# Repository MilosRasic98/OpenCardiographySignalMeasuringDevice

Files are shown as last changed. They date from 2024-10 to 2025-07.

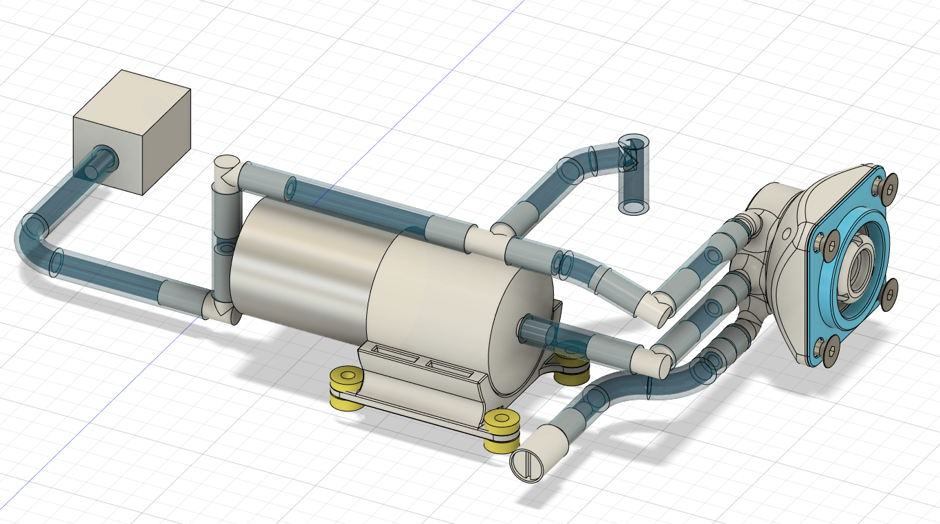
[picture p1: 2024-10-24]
Pictures/Mechanical/cad_pneumatics.PNG

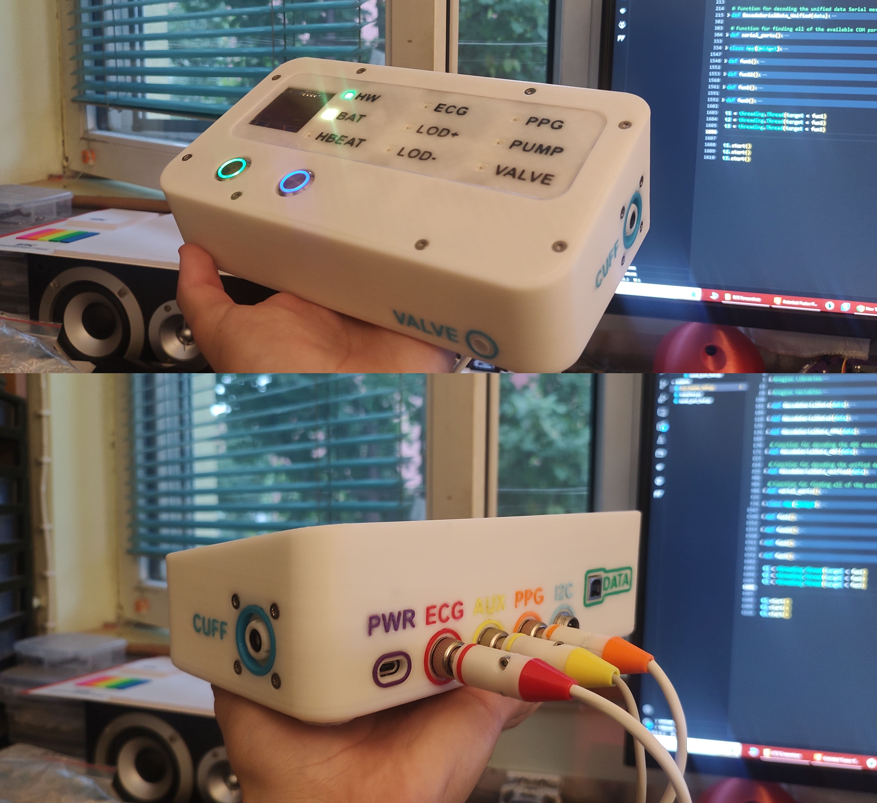
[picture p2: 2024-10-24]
Pictures/Mechanical/finishedproject.jpg

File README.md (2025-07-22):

# OpenCardiographySignalMeasuringDevice

**VIDEO OUT WITH DETAILED PROJECT EXPLANATIONS - CHECK BELOW!**

**DISCLAIMER: THIS IS A DEVICE INTENDED SOLELY FOR RESEARCH PURPOSES AND NOT A MEDICAL DEVICE INTENDED FOR CLINICAL OR DIAGNOSIS USE.**

This repository covers the development process of hardware and software and results analysis, for an open-source Cardiography Signal Measuring Device. On this page, you will be able to find all of the CAD files for the 3D printed parts, Gerber files for PCB fabrication, all of the code needed for the project, and test results of the data analysis. If you have any questions or comments, feel free to contact me! The main goal of the project was to be able to record, store, and analyze these signals:

1. Arm Cuff Air Pressure Signals
2. Electrocardiography Signals (ECG)
3. Phonocardiography Signals (Stethoscope)
4. Photoplethysmography Signals (PPG)

Through this project, I wanted to test out different algorithms for measuring blood pressure either by using just the air pressure signals from the arm cuff or those signals in combination with the other measurements, at the bottom of this page, you can take a look at the results. This project was developed as my Master's Thesis project at the University of Belgrade—School of Electrical Engineering (www.etf.bg.ac.rs), under the mentorship of Prof. Nadica Miljković. In the two pictures below you can see how the finished device looks and the design of the graphical interface for controlling the device.

For more detailed explanations about everything from electronics, to 3D printing, to measurements and data analysis, click the thumbnail below to check out the video!

Watch the video (https://www.youtube.com/watch?v=5UgFEHPnKJY)

Details and discussion about the project can be found on the Element14 Community: [E14 - CardiographyProject](https://community.element14.com/challenges-projects/element14-presents/project-videos/w/documents/71947/building-an-open-source-blood-pressure-heart-signal-monitor----episode-674?ICID=HP-674-Building-an-Open-Source-Blood-Pressure-Signal-Monitor-JULY25-WF4122160)

For things like the BOM and the implemented commands, please check this Google Sheet which is updated as soon as something new is added: https://docs.google.com/spreadsheets/d/1H5B5Kw3XJPlpduM7bu2WPejcbya2c3x0Nj9kcexb-uc/edit?usp=sharing

The project is featured in the MagPi Magazine issue 150, you can check it out here: https://magpi.raspberrypi.com/issues/150

You can take a look at the CAD models and download them from Printables as well:
1. Main Device: https://www.printables.com/model/1052466-open-cardiography-signal-measuring-device 
2. PPG Clamp: https://www.printables.com/model/1052459-ppg-clamp 

finishedproject

ThePerfectScreenshot

## Mechanical Design

The case and all of the necessary components have been 3D printed out of PLA on the Creality K1C, you can find all of the STL files as well as STEP files in the CAD files directory. Since everything was printed on a single-color 3D printer, all of the different colored inlays were glued in during the assembly process. At the back of the device GX12 connectors are used, while there are two additional USB ports, type C for charging, and type B for data (charging currently not validated, more on that later). The case houses the main custom PCB, the 18650 LION battery, and the whole pneumatic setup needed for blood pressure measurement. In the pictures below, you can see the pneumatic setup, as well as how everything is packed inside the case.

cad_pneumatics

cad_inside1

## Electronics

For electronics, a custom 4-layer PCB has been developed that uses the Raspberry Pi Pico W as the microcontroller for controlling everything. In the electronics directory, you can find the full schematics and also find the Gerber files necessary for manufacturing this PCB. The device is controlled over serial communication, and that is also how the data is sent over to the PC. These are some of the main features of the electronics:

1. Isolated USB communication - The USB data connector is galvanically isolated from the rest of the electronics so that it's safe to use, it will act as a normal USB device when connected to a PC.
2. 3V3 Buck-Boost regulator - Ensures that the device stays operational when the battery voltage drops below 3.3 V.
3. 6V boost regulator - Powering the air pump and air valve for the blood pressure measurement process.
4. Pressure Sensor Amplification - For amplifying the signal from the pressure sensor, an instrumentation INA826 amplifier has been used.
5. Stethoscope Conditioning Signals - The original idea was to use a stethoscope with an AUX output, 3 different circuits are present on the PCB for conditioning the signal so that it can be safely measured with the Pi Pico W ADC. There is a DIP switch for disabling individual circuits.
6. AD8232 ECG - The AD8232 is used for measuring the ECG signals, it was designed according to the datasheet for measuring ECG with 3 electrodes so that the signal can be analyzed for morphology.

The PCB can be powered ON by either using a switch or a button and then latching the EN pin on the buck-boost converter using the Raspberry Pi Pico W. The finished PCB design (V1) is shown in the picture below and below that is the PCB during the testing process.

pcb2d

PXL_20240524_074411466~2

For the sake of proper USB isolation and noise reduction around the switching converters, PCB cutouts, and plane breaks were added where necessary, as can be seen in the pictures below.

usbiso

buckboost_layout

### ERRORS

If you plan on pursuing this project further, below are the mistakes found during the testing process.
1. The Q6 transistor in schematic 1-Power has been flipped, meaning that the protection circuit is not validated. A quick fix is to solder a wire from BAT- to GND.
2. The isolated power supply was not working as it was supposed to. - Needs further testing.
3. The pinout on the pressure sensor is wrong.

## Software

The software for this project is currently split into three different codes and is written in C++ and Python. You can find all of the codes in the directory Software on this GitHub repo.

1. Raspberry Pi Pico Firmware - C++ - Arduino IDE -  Code that communicates with the PC over serial, controls all actuators and gathers data from the sensors.
2. Graphical Interface - Python - Visual Studio Code - Code that enables easy use of the device and shows all of the measurements in real-time. It also enables users to record all of the data into a CSV file.
3. Data Analysis - Python - Google Colaboratory - Code that analyses all of the data recorded and stored in the CSV directories.

## Additional Hardware

Besides the main device that has been shown above, there are three more things developed that are used with this device. These include the PPG clamp, a custom stethoscope, and an apparatus for calibrating the pressure sensor. If you intend only to measure ECG signals, none of these are needed, however, if you want to measure the air pressure inside the arm cuff, you'll need a way to calibrate the system, for which the apparatus is used. Also, if you want to have PPG or stethoscope measurements, you'll need them as well.

### PPG Clamp

The mechanical parts of the PPG clamp are 3D printed out of PLA as well, and the clamp is made around a MikroElektronika Oxy 5 Click, which interfaces with the system over I2C. While the outside clamp is not necessary, it provides constant pressure of the finger on the sensor, and it also blocks out outside light which helps with having better measurements. The clamp is shown in the picture below.

ppg_joines

### Stethoscope

The stethoscope that everyone has seen is an analog device that amplifies the sound so that the doctor can listen to different things such as breathing or listen to how the heart is beating. To connect this analog device to the rest of the system, the earphones were removed and a small piezo microphone was inserted into a tube so that it forms an air-tight seal. This microphone was then connected to an amplifier circuit that then goes to the analog pin of our device. The stethoscope is shown in the picture below.

stethoscope_merged

### Pressure Sensor Calibration Apparatus

When looking at the pressure sensor datasheet, the main thing we can see is that it has a linear response to the pressure. The problem here is that we are using a potentiometer to adjust the amplification, so we don't know what voltage translates to what pressure (We can always do calculations based on the potentiometer resistance and the INA826 datasheet, but it's more accurate to confirm using a calibration apparatus). This is why the calibration apparatus has been made, it can be seen in the pictures below.

PXL_20240521_131159092 MV~2

PXL_20240521_131219779 MV~2

The way the apparatus works is by being able to keep a constant pressure in the system that can be adjusted using the two screws pushing the two plungers of the syringes. In the front, there are three air pressure gauges (one is enough, three were used to do cross-validation). We want to use this apparatus by first connecting the apparatus to the pressure sensor on our PCB and then slowly adjusting the potentiometer and the apparatus so that we get to the point where we are reading 3.3 V at 40 kPa (300 mmHg). This ensures that we can cover the whole possible range while measuring blood pressure while also maximizing the capabilities of the ADC on the Pico W. While it would be enough to test in two points since the manufacturer specified a linear response, calibration was done in 40 points to ensure the sensor is working properly. Results of the calibration process are shown below, where the dots show the individual measurements, and the line is estimated using the least mean square method.

GrafikKalibracije

## Testing Process

The testing was done by comparing the results to a commercially available device. For this, the Wellue BP2 was used since it gives the Mean Arterial Pressure (MAP) measurement, besides the Systolic (SYS), Diastolic (DIA), and heart rate (HR) measurements. The person is supposed to first sit on a chair for at least 5 minutes with legs on the floor. After that, the initial measurement with the commercial device should be conducted. When that is complete, there should be at least a minute between consecutive measurements. To properly measure the signals, follow the picture below.

ElectrodePlacement

When everything is connected as shown in the picture below, connect the system using a USB cable. In the GUI connect to the device by selecting the proper COM port and setting the baud rate to 115200. After that, enable the signals you want to record, and start the stream. When you want to start recording the measurements, enter the CSV file name and click record. This can be seen in a short demo video below, click on the picture to open the video.

IMAGE ALT TEXT HERE (https://www.youtube.com/watch?v=Ox0LqK-V76g)

## Results

In this section, I will showcase the results calculated based on the measurements with the device. Before I start showing graphs, I'll give a short introduction to how blood pressure is measured both manually and automatically. This of course is only considering non-invasive methods, and even in 2024, the gold standard for blood pressure measurement is still the manual approach which includes a regular stethoscope and a hand pump.

### Manual Blood Pressure Measurement

Manual blood pressure measurement takes advantage of what is known as Korotkoff sounds. These are the sounds that can be heard using the stethoscope during the process of measuring blood pressure. This process works by putting an arm cuff above the elbow and starting to inflate it using the hand pump. As the pressure inside the cuff goes up, the cuff squeezes the arm and constricts blood flow through the brachial artery, until the pressure in the cuff goes above the SYS pressure. At that moment, blood circulation is cut off. The doctor measuring blood pressure can recognize this by hearing no sounds on the stethoscope, at that moment, he starts opening a small manual valve to slowly let the air out of the cuff. At the moment that the pressure in the cuff equalizes with the SYS pressure, Korotkoff sounds appear, which present themselves as "banging" noises on the stethoscope. The moment the sounds appear is the moment when we look at the gauge and read the SYS pressure. As the pressure continues to drop in the cuff, the Korotkoff sounds will persist as long as the pressure in the cuff is above the DIA pressure. During this time, the blood flow is turbulent. As the pressure in the cuff falls below the DIA pressure, the blood flow becomes linear and the Korotkoff sounds disappear. This is the moment where we read the DIA pressure on the gauge. This process is illustrated in the picture below, where the blue line represents the air pressure in the cuff, while the red line shows the blood pressure we are measuring.

ManualBPM

### Automatic Blood Pressure Measurement

With the advance of technology, many devices with different algorithms have been developed for measuring blood pressure automatically, and are something that can be found in pretty much every household today. One thing to note here is that these devices work on completely unknown algorithms, and there is no proper way of validating the results they calculate. This is why the manual method is still considered a gold standard in 2024 and also why the criteria for blood pressure monitors is rather low. A blood pressure monitor is considered to be in class A (highest class) if its measurements are in +/- 15 mmHg for the SYS pressure in 85% of the measurements. Considering that if the SYS is 135 mmHg, the device is considered working properly if it's between 120 mmHg and 150 mmHg, this poses a big issue of how trustworthy these devices are.

I'll explain here one of the more well-known algorithms for estimating blood pressure which works by analysing the envelope of the signal. To give you a better idea of what I'm talking about, I'll first show you the pressure measurement in the cuff during a blood pressure measurement test, which is shown in the picture below.

BPM_fig2_PritisakUTokuIspumpavanja

The picture above shows only the part of the signal while the arm cuff is deflating. If you take a closer look at the signal, you can see that pulsations start appearing as the pressure decreased, their amplitudes grow, and at one point the amplitude starts going down. This is what we want to analyze but to do that, we need to pass the signal through a high pass filter and detrend the signal. Once we do that, we can estimate an envelope for that signal and continue with the algorithm. The moment in which the envelope reaches its maximum value is the moment in which the air pressure in the cuff is equal to the MAP. Now, according to the algorithm I am using (Sapinsky) we take the value of the MAP amplitude and find the moments in time where the envelope is equal to 40% of MAP and 80% of MAP. These are the moments at which we measure the SYS and DIA pressures. This is illustrated in the picture below.

AutomaticBPM

### Signal Analysis

In this section, I'll give a short demonstration of signal analysis on the measurements I recorded during testing. This will include analyzing the data from the arm cuff, PPG, stethoscope, and ECG. The code I used for analyzing this data as well as a data set that was analyzed here can be found in this GitHub repository, so you can play around with the data if you want! At the end of the signal analysis, I'll show how the results hold up to the commercial device.

#### Arm Cuff Pressure Signal

I'll begin by analyzing the arm cuff pressure signal since that was the main focus of my work. First, in the picture below is the signal in the arm cuff during the whole blood pressure measuring procedure. You can see the pressure rising steeply while the pump is turned on, as well as the pressure going down as the cuff slowly deflates with a sudden release at the very end when the electromagnetic valve is triggered.

BPM_fig1_PritisakUManzetniUTokuMerenja

As mentioned in the algorithm explanation above, we are interested in the part of the signal where the arm cuff is being slowly deflated, as this part of the signal contains the data we are interested in. For this test, the arm cuff was inflated manually to a high pressure, modern devices do a rough estimate of the SYS pressure while inflating the cuff and they inflate it about 30 mmHg above that value and then they start the deflation process. This is done for patient comfort since high pressures can be painful on the arm. In the picture, you can see the part of the signal where the arm cuff is deflating.

BPM_fig2_PritisakUTokuIspumpavanja

Before estimating the envelope, we need to filter the signal first. The two pictures below show the signal filtering process, if you're interested in the details about the filter, check the code where you can see the filter type, order, and cut-off frequency.

BPM_fig8_Detrending

BPM_fig3_PritisakUTokuIspumpavanja-Filtriran

Now that the signal has been filtered, we can estimate the envelope of the signal. Besides the envelope, we can find the peaks in the signal which correlate to the heart beats, so we can calculate the heart rate from them.

BPM_fig5_PritisakUTokuIspumpavanja-Filtriran-Pikovi-Anvelopa

As you can see from the picture above, the signal is not ideal. We don't have the ideal envelope as expected and as was shown in the drawing above. Nevertheless, this signal can still be used for estimating the SYS and DIA pressures. Before we do that, we need to find the max value of the envelope to find the moments for measuring the SYS and DIA pressures. This is shown in the picture below.

BPM_fig6_PritisakUTokuIspumpavanja-Filtriran-Pikovi-Anvelopa-SYS-DIA-MAP

Using those time moments that we calculated based on the graph in the picture above, we can return to the original pressure signal, and see what was the pressure in the arm cuff in those moments. This is how we calculate the MAP, SYS, and DIA, while we use the peaks for calculating the HR. Below is the picture of that, you can see the final results at the bottom of this section with the comparison.

BPM_fig7_PritisakUTokuIspumpavanja-SYS-DIA-MAP

#### Stethoscope Signal Analysis

I wanted to use the signal from the stethoscope as an experimental way of estimating the SYS pressure based on the description of how we measure blood pressure using Korotkoff sounds. My idea was to try and see when the pulsations become somewhat regular, or better said when they start matching the heart rhythm and taking the beginning of that as the moment for reading the SYS pressure. In the two pictures below, you can see the signal from the stethoscope recorded at the same time as the air pressure signal above as well as the stethoscope signal during the arm cuff deflation phase.

AUX_fig1_CeloMerenjePritiska

AUX_fig2_Ispumpavanje

Here I detected the peaks, and you can see a clear difference from the third peak and how there are no missed pulsations. This is the time moment I wanted to use for the SYS pressure and we can also use those peaks to calculate the HR. 

AUX_fig3_Ispumpavanje-Vrhovi

Using the time moment of the third peak, we return to the pressure signal in the arm cuff to read the pressure at that moment.

AUX_fig5_MerenjeSistolnogPritiska

#### PPG Signal Analysis

PPG works by measuring the reflected light at different wavelengths, and based on that signal, we can calculate both the HR and the blood oxygen saturation. For now, I will only look at the signal for measuring the HR, because we can use it really nicely for estimating the DIA pressure. As I've mentioned above when the pressure in the arm cuff is dropping, the blood flow in the arm goes from turbulent to laminar, and the PPG sensor is designed for measurements when the blood flow is laminar. We can see this in the signal by the first flatlining signal, followed by pulsations as the laminar blood flow returns to the arm. In the two pictures below, you can see the PPG signal from the whole measurement and then only from the section where the arm cuff is deflating.

PPG_fig1_FotopletizmografskiSignalUTokuMerenjaKrvnogPritiska

PPG_fig2_FotopletizmografskiSignalUTokuIspumpavanjaManzetne

I then passed the signal through a filter in the same way I did with the pressure signal shown above. So the two pictures below show the signal filtering process.

PPG_fig6_Detrending

PPG_fig3_FiltriranPPGSignal

What we want to do now is find the peaks in the signal to find the moment when the pulsations appear again. This is the moment we will use to measure the DIA pressure. This is shown in the pictures below.

PPG_fig4_FiltriranPPGSignal-Vrhovi

PPG_fig5_PPG-IzmerenDijastolniPritisak

#### ECG Signal Analysis

In the end, we have the ECG signal. While there is some experimental work for measuring blood pressure by measuring the time delay between R peaks in the ECG signal and the pulsations on the PPG, I will only use the ECG to validate the HR measurement of the other methods and show the morphology of a recorded heartbeat. A section of the measurement is shown in the picture below.

ECG_fig2_EKG_DeoMerenja

By detecting the R peaks, we can easily calculate the HR. We can also use that data from ECG to analyze heart rate variability which is a topic I won't be getting into here. But you can see the time between heartbeats in the picture below.

ECG_fig3_EKG_HRV

And in the end, you can see a single heartbeat that was extracted from the measurement.

ECG_fig4_EKG_JedanOtkucaj

### Final Results

Before showing you the final results from the signal analysis, let's take a look at the measurement done with the Wellue BP2 Blood Pressure monitor. Its results are shown in the picture below.



Now, let's compare that to the results we estimated from our measurements, this is shown in the table below.

| | Mean Arterial Pressure (MAP) [mmHg] | Systolic Pressure (SYS) [mmHg]  | Diastolic Pressure (DIA) [mmHg] | Heart Rate (HR) [BPM] |
| ------------- | ------------- | ------------- | ------------- | ------------- |
| Wellue BP2 | 93 | 130 | 72 | 81 |
| Arm Cuff Air Pressure | 91 | 132 | 79 | 78 |
| Stethoscope | X | 143 | X | 80 |
| PPG | X | X | 75 | 80 |
| ECG | X | X | X | 80 |

As you can see from the table, the results obtained from the data analysis are pretty good when compared to the commercial device. This is of course one data set and all of this requires much more testing, but it's still rewarding to see promising results. Estimating the SYS pressure using the stethoscope didn't give the best estimation, but this needs more experimenting with things like stethoscope placement, pressure, and so on. One thing that gave really good results was the PPG estimation of the DIA pressure, it's more spot-on than the analysis of the pressure in the arm cuff.

If you have any comments or questions about anything you've seen here, feel free to write to me! Some of the pictures have writing in Serbian but the graphs should be clear based on the units, if you're still struggling with any of that, feel free to contact me!

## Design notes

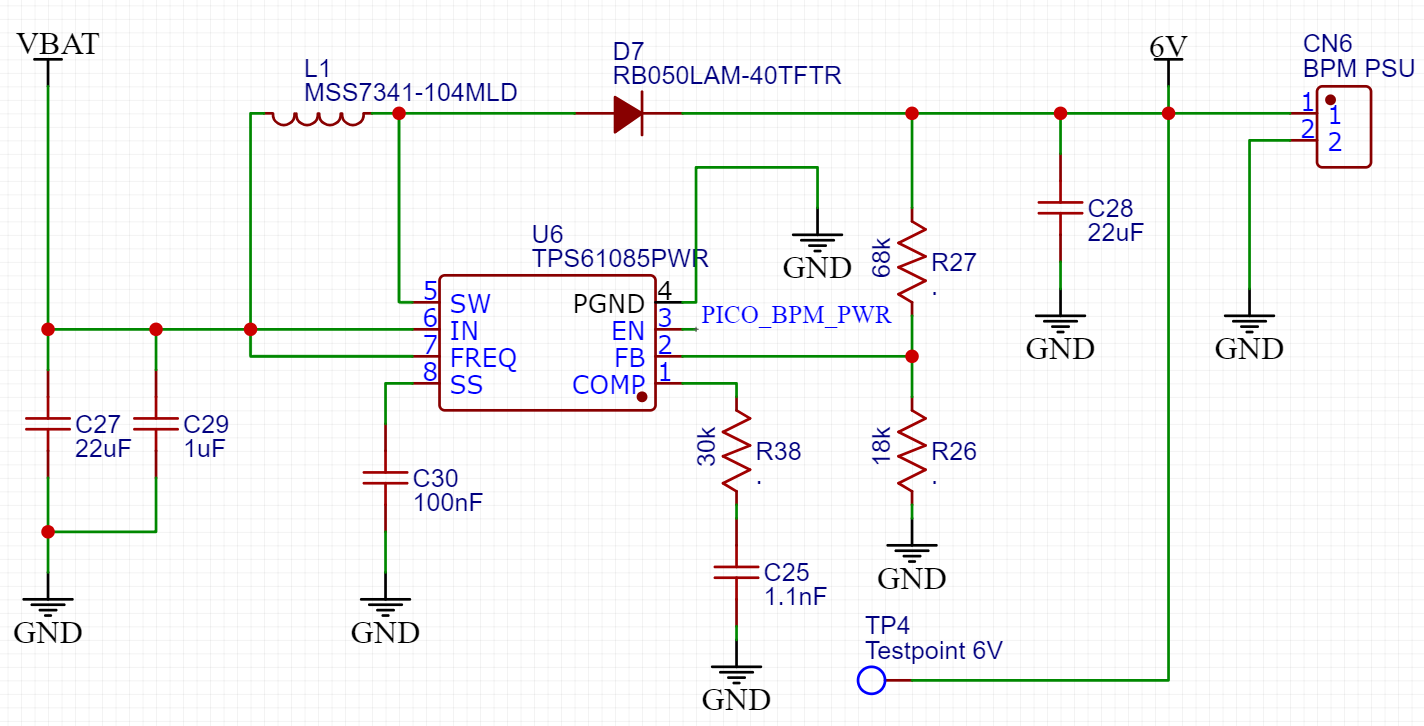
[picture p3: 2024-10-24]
Pictures/Electronics/boost.PNG

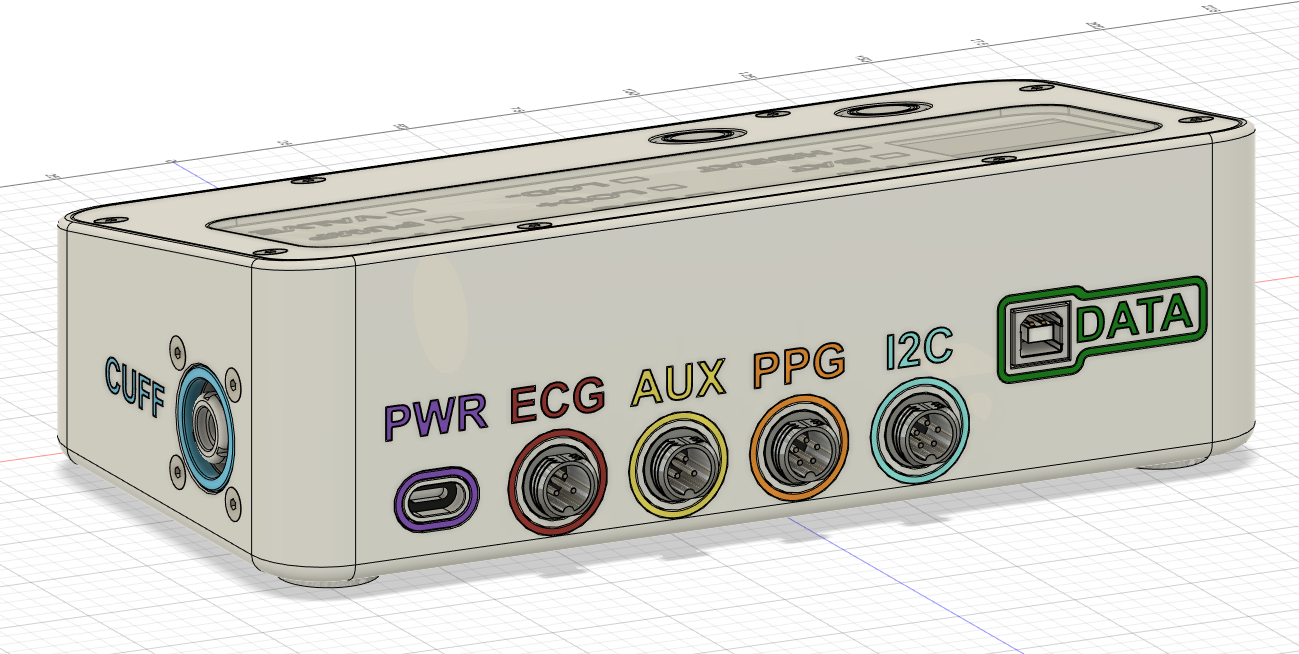
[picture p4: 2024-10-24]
Pictures/Mechanical/cad_backview.PNG

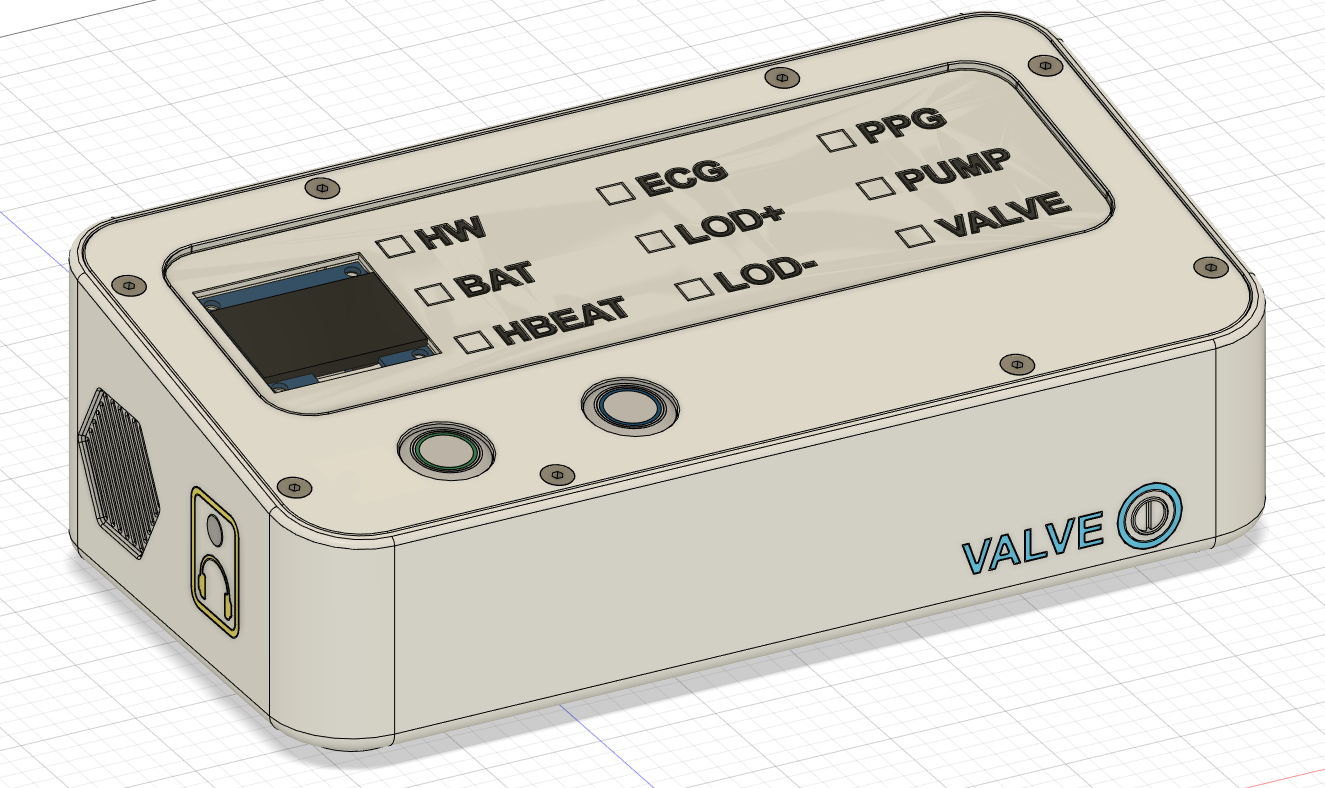
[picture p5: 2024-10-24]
Pictures/Mechanical/cad_frontview.PNG

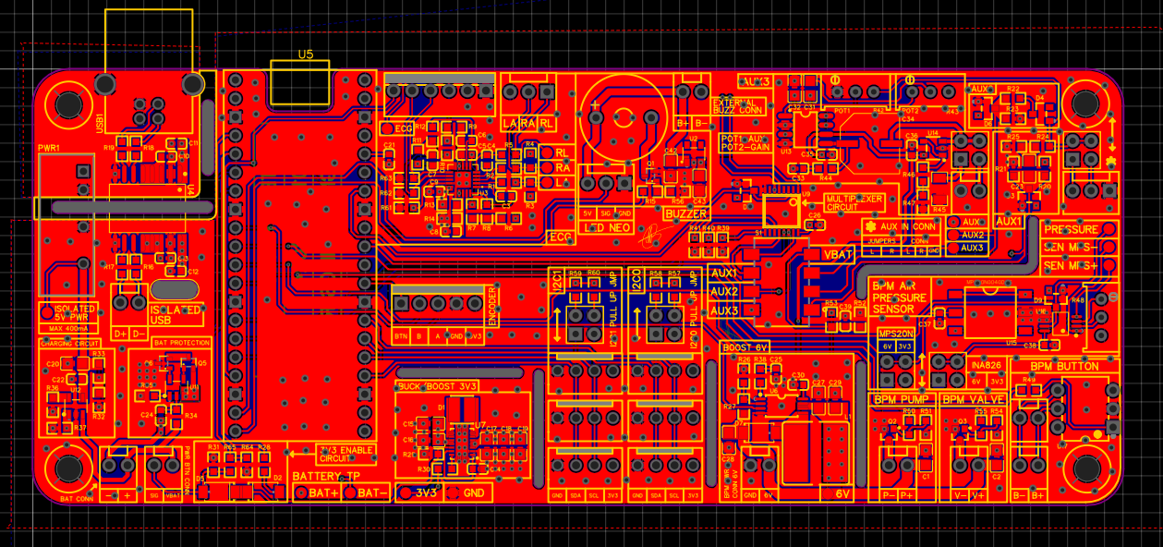
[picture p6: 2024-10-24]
Pictures/Electronics/PCB_1_TopLayer.PNG

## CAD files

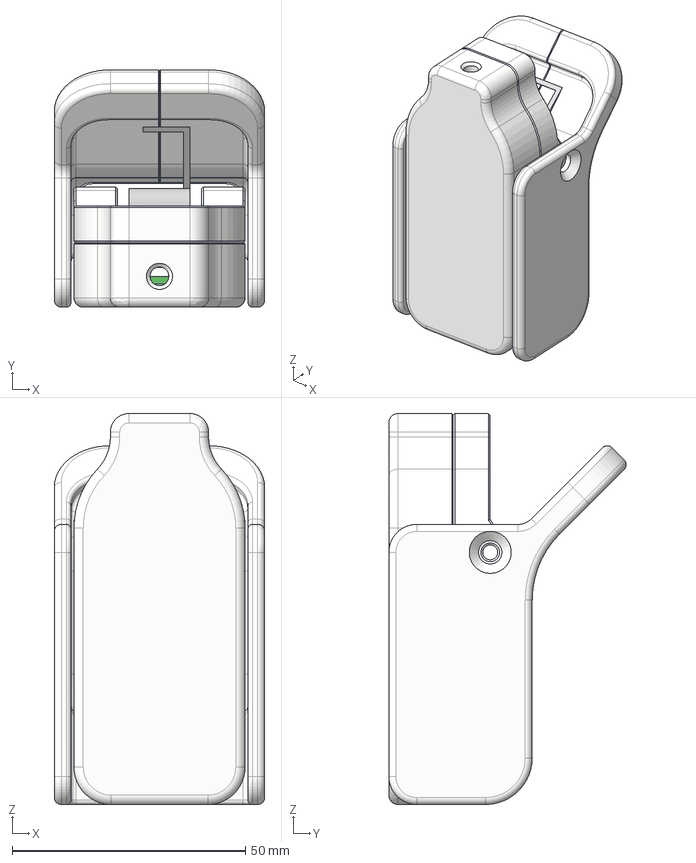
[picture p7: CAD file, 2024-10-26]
CAD/PPG/STEP/Oximeter Clamp V1 v3.step
45.1 x 50.9 x 83.8 mm
Board
User_Library-SMD_CAPACITOR0402 x 7
User_Library-SMD_CAPACITOR0603 x 3
led_0805_green
User_Library-SOT23-6-2
MAX30101
User_Library-PinHeaderX5-1_PinHeaderX5_Body_1 x 4
User_Library-PinHeaderX5-1_PinHeaderX5_Pins_1 x 4
User_Library-R_0805 x 2
User_Library-R_0402 x 6
User_Library-US8_Package_(8US8_8SM8_8DSBGA)_2_4x2_1x0_9
Sot353
Perfboard
Lower Body
Axle Mount
Spring
Cover V1 Half 2
Cover V1 Half 1

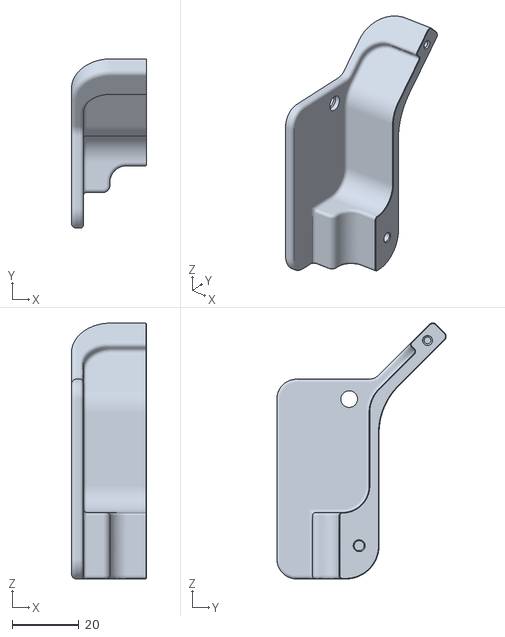
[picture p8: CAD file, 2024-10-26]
CAD/PPG/STL/Cover V1 Half 2.stl
22.5 x 50.9 x 76.9

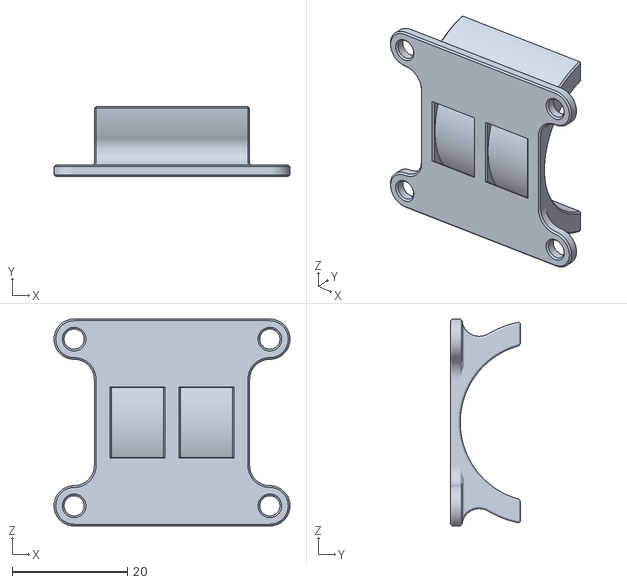
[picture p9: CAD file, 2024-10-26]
CAD/STL/Air Pump Mount.stl
41.0 x 12.2 x 36.0

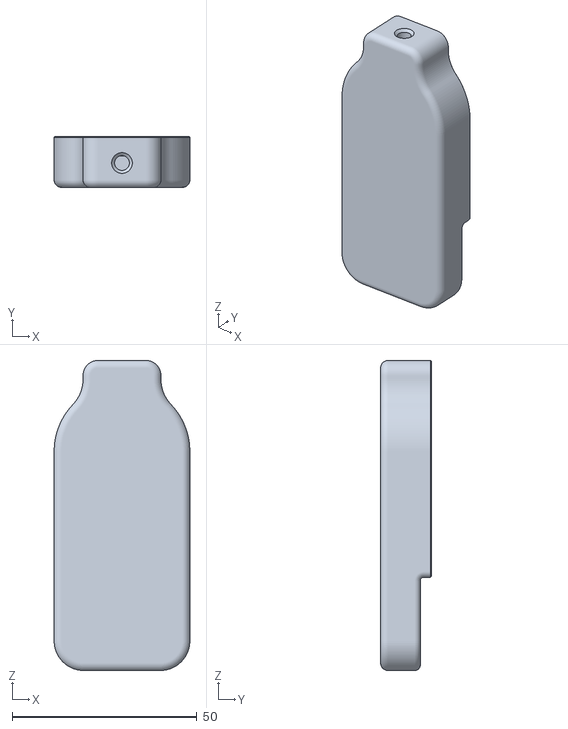
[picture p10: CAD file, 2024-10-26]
CAD/PPG/STL/Lower Body.stl
36.7 x 13.7 x 83.8

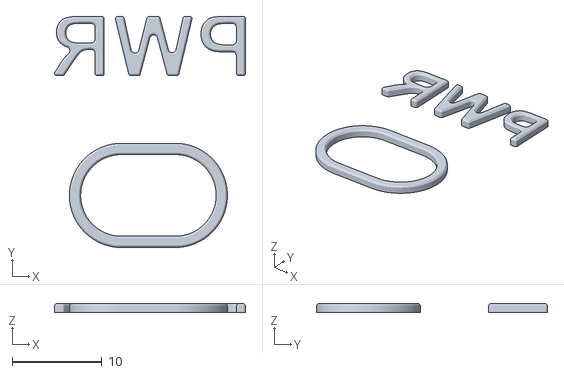
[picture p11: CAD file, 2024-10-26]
CAD/STL/PWR Sign and Ring.stl
21.3 x 25.8 x 1.00

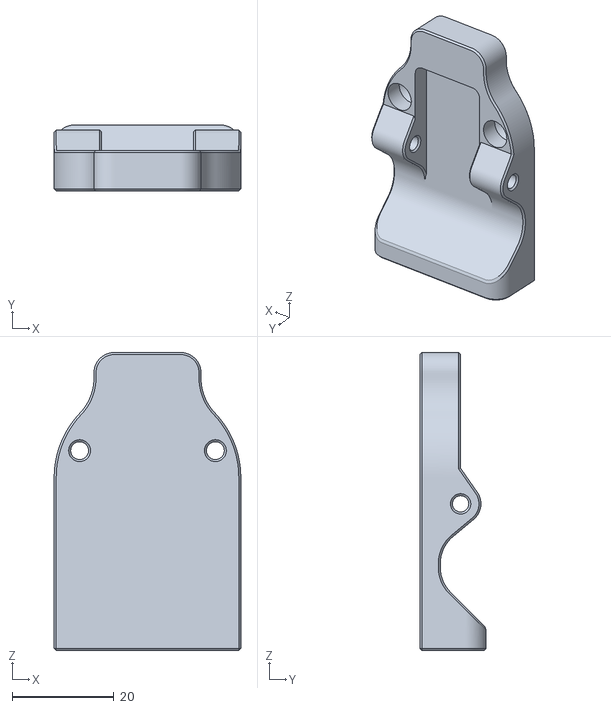
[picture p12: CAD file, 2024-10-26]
CAD/PPG/STL/Axle Mount.stl
36.7 x 13.0 x 58.6

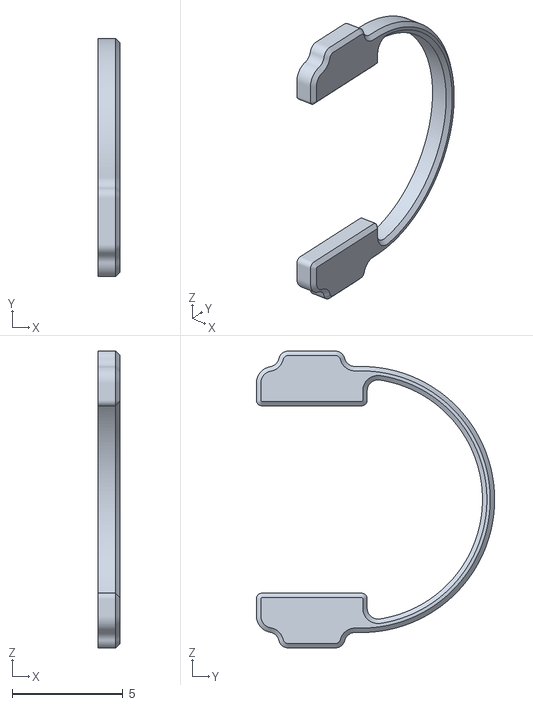
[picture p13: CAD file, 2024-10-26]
CAD/STL/Headphones Sign.stl
1 x 10.7 x 13.4

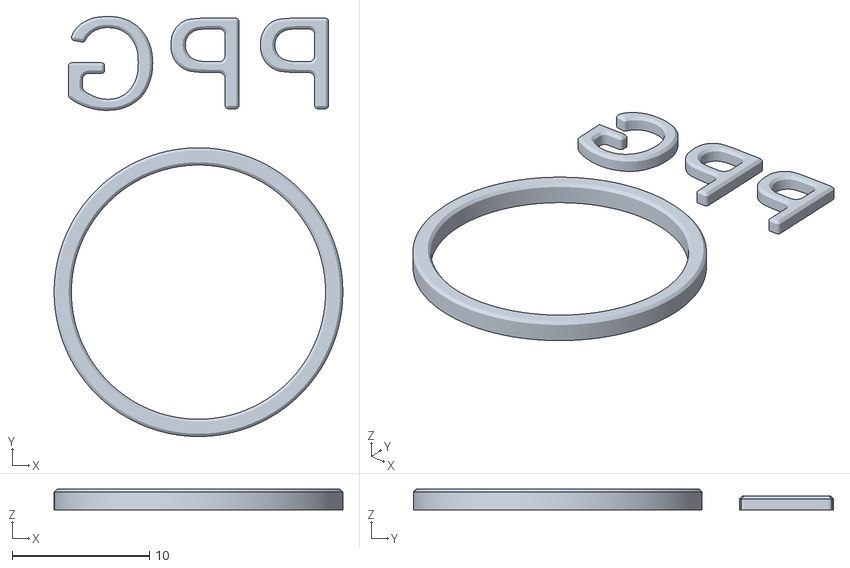
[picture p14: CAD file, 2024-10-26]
CAD/STL/PPG Sign and Ring.stl
21.0 x 30.6 x 1.50

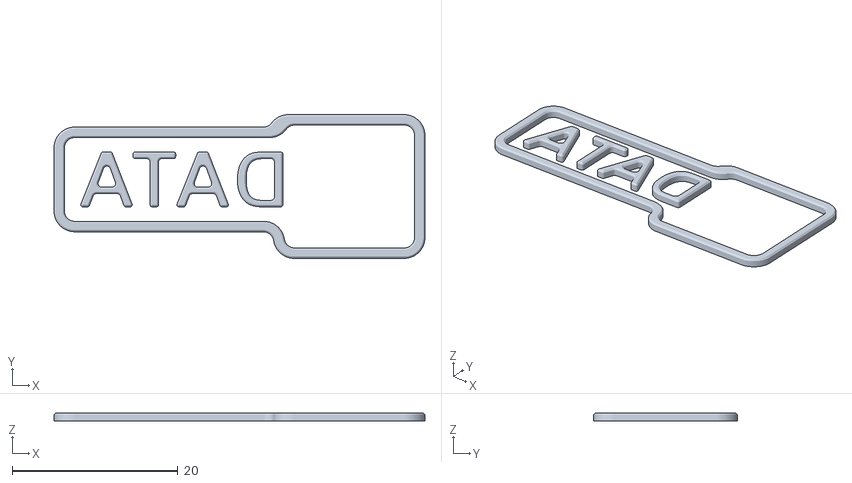
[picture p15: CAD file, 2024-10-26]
CAD/STL/Data Sign and Ring.stl
44.7 x 17.3 x 1.00

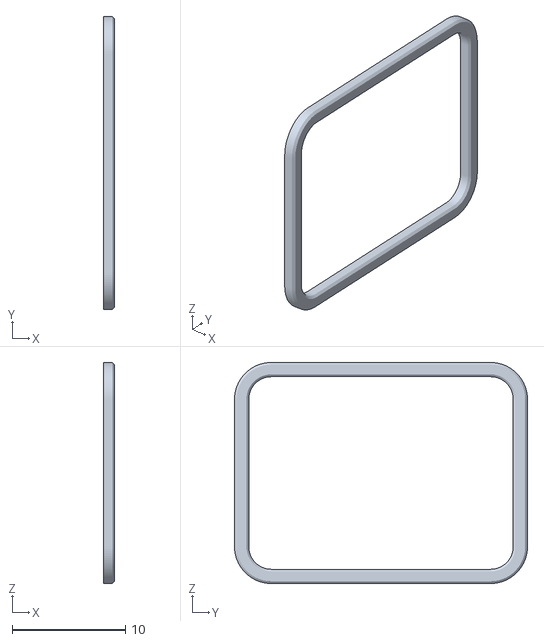
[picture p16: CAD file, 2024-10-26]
CAD/STL/Headphone Ring.stl
1 x 25.9 x 19.5

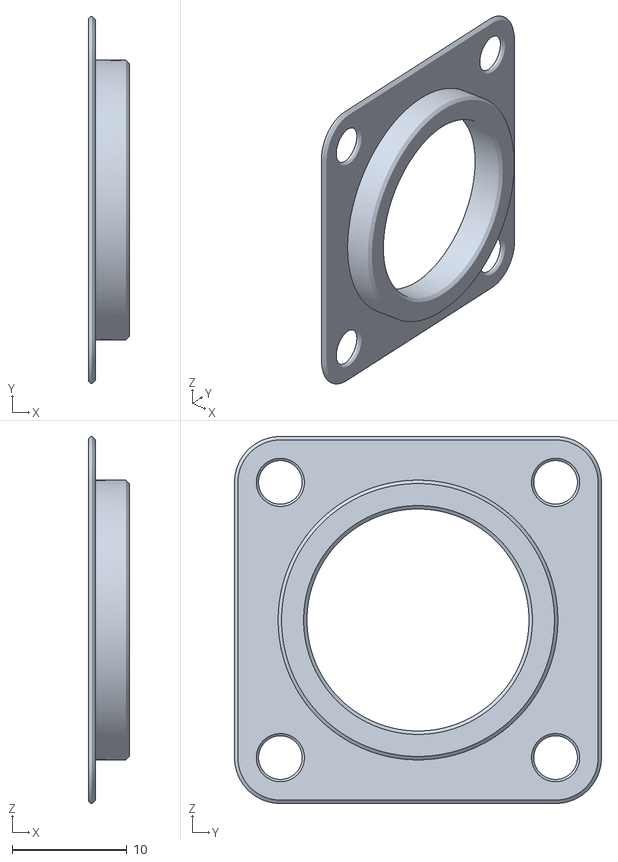
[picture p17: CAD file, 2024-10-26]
CAD/STL/Body End Triple Pipe Blue Top.stl
3.54 x 32.0 x 32.0

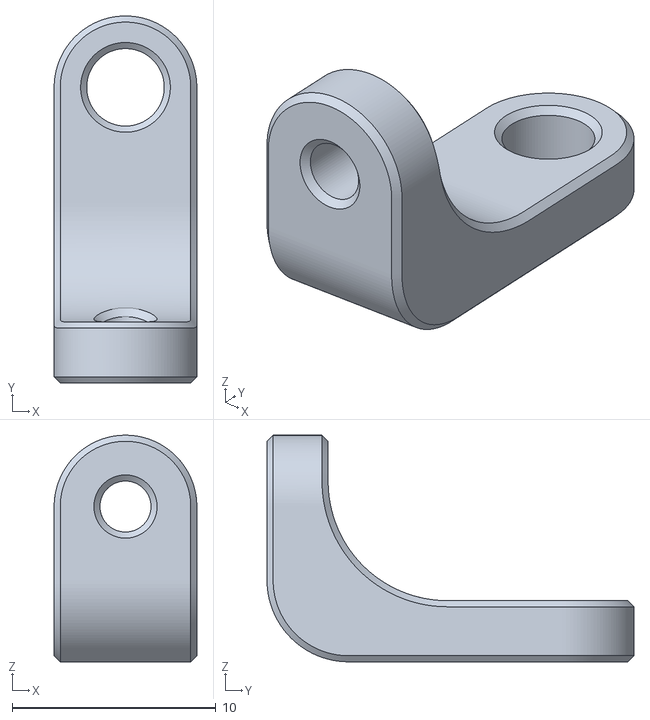
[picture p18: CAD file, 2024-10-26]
CAD/STL/PCB Bracket.stl
7.00 x 18.0 x 11.1

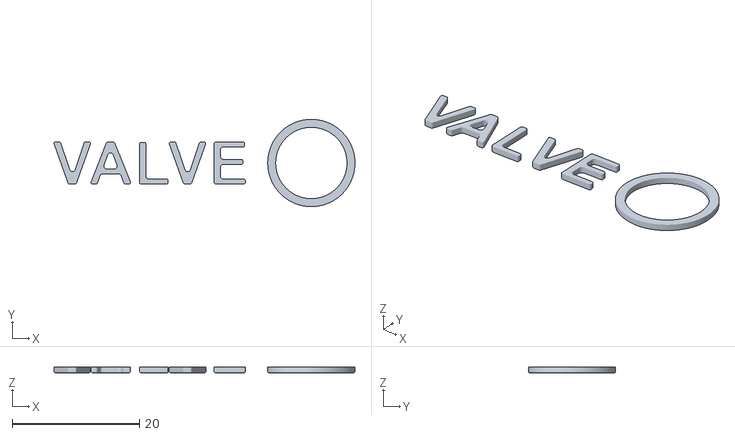
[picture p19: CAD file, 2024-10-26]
CAD/STL/Valve Sign and Ring.stl
47.3 x 13.7 x 1.00

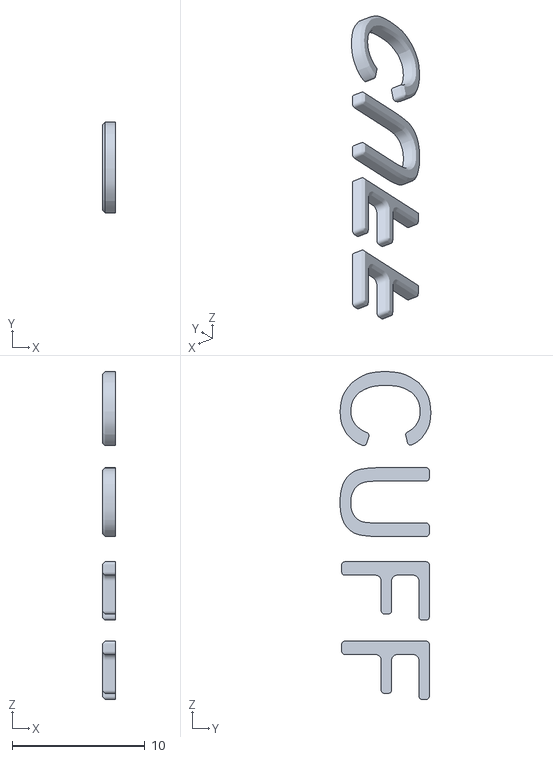
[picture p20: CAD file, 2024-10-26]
CAD/STL/Cuff Sign.stl
1.00 x 6.84 x 24.7

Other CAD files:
CAD/PPG/STL/Cover V1 Half 1.stl
CAD/STL/ECG Sign and Ring.stl
CAD/STL/Body End Triple Pipe Shortened.stl
CAD/STL/LED and Screen Bracket.stl
CAD/STL/AUX Sign and Ring.stl
CAD/STL/Audio Jack Mounting Bracket.stl
CAD/STL/Body Bottom Part V1.stl
CAD/STL/Em Valve Bracket.stl
CAD/STL/I2C Sign and Ring.stl
CAD/STL/Lid.stl

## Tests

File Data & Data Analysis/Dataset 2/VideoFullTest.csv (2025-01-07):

ECG_VALUE | ECG_TIME | BPM_VALUE | BPM_TIME | AUX_VALUE | AUX_TIME | PPG_VALUE | PPG_TIME
1892 | 856347 | -4.865679999999999 | 856347 | 51 | 856347 | 62522 | 856348
1792 | 856349 | -4.94256 | 856349 | 51 | 856349 | 62483 | 856350
1987 | 856365 | -4.94256 | 856365 | 52 | 856365 | 62408 | 856359
1899 | 856371 | -4.865679999999999 | 856371 | 51 | 856371 | 62378 | 856369
1961 | 856381 | -4.94256 | 856381 | 51 | 856381 | 62447 | 856379
2070 | 856401 | -4.865679999999999 | 856401 | 51 | 856401 | 62449 | 856399
2050 | 856405 | -4.865679999999999 | 856405 | 51 | 856405 | 62449 | 856399
1987 | 856407 | -4.865679999999999 | 856407 | 51 | 856407 | 62451 | 856407
1931 | 856409 | -4.94256 | 856409 | 51 | 856409 | 62461 | 856409
1890 | 856411 | -4.94256 | 856411 | 51 | 856411 | 62461 | 856409
1896 | 856415 | -5.0194399999999995 | 856415 | 51 | 856415 | 62461 | 856409
1948 | 856417 | -4.94256 | 856417 | 51 | 856417 | 62470 | 856417
2025 | 856419 | -4.94256 | 856419 | 51 | 856419 | 62485 | 856419
2112 | 856421 | -4.94256 | 856421 | 51 | 856421 | 62485 | 856419
2185 | 856425 | -4.865679999999999 | 856425 | 52 | 856425 | 62485 | 856419
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

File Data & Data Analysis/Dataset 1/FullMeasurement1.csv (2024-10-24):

ECG_VALUE | ECG_TIME | BPM_VALUE | BPM_TIME | AUX_VALUE | AUX_TIME | PPG_VALUE | PPG_TIME
2069 | 204485 | -4.7888 | 204485 | 53 | 204485 | 64514 | 204479
2113 | 204489 | -4.7888 | 204489 | 52 | 204489 | 64533 | 204489
2043 | 204499 | -4.711919999999999 | 204499 | 53 | 204499 | 64582 | 204497
2067 | 204519 | -4.7888 | 204519 | 54 | 204519 | 64602 | 204520
2033 | 204541 | -4.7888 | 204541 | 53 | 204541 | 64590 | 204542
2133 | 204549 | -4.63504 | 204549 | 53 | 204549 | 64596 | 204550
2132 | 204551 | -4.7888 | 204551 | 53 | 204551 | 64620 | 204552
2048 | 204559 | -4.711919999999999 | 204559 | 53 | 204559 | 64606 | 204560
2033 | 204561 | -4.7888 | 204561 | 53 | 204561 | 64629 | 204562
2083 | 204569 | -4.558160000000001 | 204569 | 53 | 204569 | 64616 | 204570
2096 | 204571 | -4.7888 | 204571 | 52 | 204571 | 64600 | 204572
2049 | 204579 | -4.711919999999999 | 204579 | 52 | 204579 | 64619 | 204580
2042 | 204581 | -4.711919999999999 | 204581 | 53 | 204581 | 64607 | 204582
2106 | 204589 | -4.7888 | 204589 | 53 | 204589 | 64621 | 204590
2120 | 204591 | -4.7888 | 204591 | 53 | 204591 | 64569 | 204592
2061 | 204599 | -4.711919999999999 | 204599 | 53 | 204599 | 64632 | 204600
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

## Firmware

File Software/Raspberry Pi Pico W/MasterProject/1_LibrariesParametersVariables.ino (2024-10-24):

/*
 *  LIBRARIES
 */
#include <Wire.h>
#include "RPi_Pico_TimerInterrupt.h"
#include "RP2040_PWM.h"
#include <DFRobot_MAX30102.h>
#include <FastLED.h>

/*
 *  PINS
 */
#define PIN_PWR_BTN     2
#define PIN_PWR_LATCH   3
#define PIN_SIG_CHARGE  4
#define PIN_MCP_CHARGE  5
#define PIN_BPM_PWR     6
#define PIN_BPM_BTN     7
#define PIN_BPM_PUMP    8
#define PIN_BPM_VALVE   9
#define PIN_MUX_A       10
#define PIN_MUX_B       11
#define PIN_MUX_C       12
#define PIN_ECG_EN      13
#define PIN_NEO_LED     14
#define PIN_BUZZ        15
#define PIN_ENC_A       16
#define PIN_ENC_B       17
#define PIN_I2C1_SDA    18
#define PIN_I2C1_SCL    19
#define PIN_I2C0_SDA    20
#define PIN_I2C0_SCL    21
#define PIN_ENC_BTN     22
#define PIN_BPM_ANALOG  26
#define PIN_ECG_ANALOG  27
#define PIN_AUX_ANALOG  28


/*
 *  PARAMETERS
 */

// GENERAL PARAMETERS
#define SAMPLING_FREQUENCY    1000      // [Hz]           Sampling frequency for the Pico ADC
#define COMM_FREQUENCY        500       // [Hz]           Communication frequnecy with the PC
#define ADC_RES               12        // [bit]          ADC resolution set in bits 10/12
#define SERIAL_BAUDRATE       115200    // [#]            Serial communication baudrate 9600/115200
#define PWM_FREQUENCY         1000      // [Hz]           PWM signal frequency     
#define SERIAL_DEBUG          true      // [true/false]   Flag that enables/disables serial debugging
#define LED_FREQUENCY         100       // [Hz]           LED timer 0 frequency
#define CON_FREQUENCY         1000      // [Hz]           Control timer 2 frequency
#define LED_TICKS             100       // [#]            Number of timer ticks before changing the LED state in normal state
#define LED_TICKS_ERROR       10        // [#]            Number of timer ticks before changing the LED state in error state
#define UNIFIED_MESSAGE       true      // [true/false]   Flag for sending a unified message over the serial port
#define PWR_OFF_HOLD          5000      // [ms]           Number of miliseconds that the blue buttons needs to be held for to turn off the device
#define NUM_LEDS              9         // [#]            Number of LEDs on the front panel

// BPM PARAMETERS
#define BPM_MAX_PUMP_DUTY     100       // [%]            Max duty cycle of the PWM signal that is controlling the pump for the BPM
#define BPM_MIN_PUMP_DUTY     0         // [%]            Min duty cycle of the PWM signal that is controlling the pump for the BPM

// AUX PARAMETERS
#define AUX_MAX_BUZZ_DUTY     100       // [%]            Max duty cycle of the PWM signal that is controlling the Buzzer
#define AUX_MIN_BUZZ_DUTY     0         // [%]            Min duty cycle of the PWM signal that is controlling the Buzzer
#define AUX_BUZZ_BEEP_DUTY    10        // [%]            Duty cycle used for the regular beeping when for example when it's indicating the pulse
#define AUX_BUZZ_BEEP_MAX     2000      // [ms]           Length of the longest allowed beep for the buzzer
#define AUX_BUZZ_BEEP_MIN     10        // [ms]           Length of the shortest allowed beep for the buzzer

// PPG PARAMETERS
#define PPG_SPO2_FREQUENCY    1         // [Hz]           Reading frequency for the SpO2 
#define PPG_IR_FREQUENCY      20        // [Hz]           Reading frequency for the PPG sensor

// CALCULATED PARAMETERS
#define COMM_PERIOD           1000000 / COMM_FREQUENCY                  // [us]   Number of us needed to achieve the desired frequency
#define LED_PERIOD            1000000 / LED_FREQUENCY                   // [us]   Number of us needed to achieve the desired frequency
#define SEN_PERIOD            1000000 / SAMPLING_FREQUENCY              // [us]   Number of us needed to achieve the desired frequency
#define CON_PERIOD            1000000 / CON_FREQUENCY                   // [us]   Number of us needed to achieve the desired frequency
#define PPG_SPO2_COUNT        SAMPLING_FREQUENCY / PPG_SPO2_FREQUENCY   // [#]    Max count value for the PPG SPO2 reading
#define PPG_IR_COUNT          SAMPLING_FREQUENCY / PPG_IR_FREQUENCY     // [#]    Max count value for the PPG IR reading

/*
 * VARIABLES
 */

// Flags
bool          flag_en_6V      =       true;     // [true/false]   Flag for turning the boost converter ON/OFF
bool          flag_pin_cng    =       false;    // [true/false]   Flag for indicating if a digital pin state change is needed
bool          error_state     =       false;    // [true/false]   Flag that indicates whether we are in an error state or not
bool          flag_pwr_latch  =       true;     // [true/false]   Flag that indicates whether we should keep the Pico W turned ON or not
bool          led_disable     =       false;    // [true/false]   Flag that indicates whether LEDs are disabled or not

// Communication
bool          flag_new_msg    =       false;    // [true/false]   Flag for showing if there is a new message on the Serial port
String        serial_msg      =       "";       // [String]       Variable for storing the message from the Serial port (Commands are received through this message)       
bool          data_stream     =       false;    // [true/false]   Flag for showing if the data stream to the PC is turned ON or OFF
volatile int  message_id      =       0;        // [#]            In the data stream, this will be the parameters used to make sure there aren't any skipped messages
String        stream_msg      =       "";       // [String]       Variable for storing the message for the DataStream
volatile bool flag_adc_msg    =       false;    // [true/false]   Flag for showing whether a new ADC message is scheduled
volatile bool flag_ppg_msg_ir =       false;    // [true/false]   Flag for showing whether a new PPG IR message is scheduled
volatile bool flag_ppg_msg_o2 =       false;    // [true/false]   Flag for showing whether a new PPG SpO2 message is scheduled       
volatile int  message1_id     =       0;        // [#]            Counter for message with ID = 1
volatile int  message2_id     =       0;        // [#]            Counter for message with ID = 2
volatile int  message3_id     =       0;        // [#]            Counter for message with ID = 3

// Blood Pressure Monitor
int           bpm_pump_duty   =       0;        // [%]            Duty cycle that is being sent to the pin connected to the BPM pump
int           bpm_valve       =       0;        // [0/1]          Variable for storing whether the valve is ON or OFF
int           bpm_opto        =       0;        // [0/1]          Variable for storing whether the optocoupler is turned ON or OFF
volatile int  bpm_adc         =       0;        // [ADC]          BPM ADC reading
volatile int  bpm_mmhg        =       0;        // [mmHg]         BPM reading converted to mmHg
bool          bpm_enable      =       false;    // [true/false]   Flag for inticating whether the BPM readings are enabled or not

// ECG
bool          flag_en_ecg     =       false;    // [true/false]   Flag for turning the ECG chip ON/OFF 
volatile int  ecg_adc         =       0;        // [ADC]          Variable for storing the latest ecg value read by the ADC
int           ecg_lp          =       -1;       // [0/1]          ECG LP signal
int           ecg_ln          =       -1;       // [0/1]          ECG LN signal
volatile int  ecg_msg_time    =       0;        // [ms]           ECG signal read time

// AUX
volatile int  aux_adc         =       0;        // [ADC]          ADC reading for the AUX channel
bool          aux_enable      =       false;    // [true/false]   Flag for indicating whether the AUX readings are enabled or disabled

// SpO2
bool          spo2_active     =       false;    // [true/false]   Flag that indicated whether our sensor is active or not
volatile int  spo2_ir         =       0;        // [#]            Variable for storing the IR value read by the MAX30102 sensor
volatile int  spo2_r          =       0;        // [#]            Variable for storing the R value read by the MAX30102 sensor
int32_t       spo2_o2         =       0;        // [#]            Variable for storing the O2 value read by the MAX30102 sensor
int8_t        spo2_o2_valid   =       0;        // [0/1]          Flag that indicates whether the O2 saturation reading is valid 
int32_t       spo2_hr         =       0;        // [#]            Variable for storing the heart rate value calculated by the MAX30102 sensor
int8_t        spo2_hr_valid   =       0;        // [0/1]          Flag that indicates whether the HR calculation is valid
volatile int  spo2_count      =       0;        // [#]            Counter for lowering the read frequency for SpO2 and HR for the MAX30102 sensor
volatile int  spo2_ir_count   =       0;        // [#]            Counter for lowering the read frequenct for IR readings for the MAX30102 sensor         
volatile int  spo2_ir_time    =       0;        // [ms]           Time of reading the IR signal from the MAX30102
volatile int  spo2_o2_time    =       0;        // [ms]           Time of reading the SpO2 values from the MAX30102
volatile int  ppg_msg_ind     =       0;        // [0/1]          Indicator for a new PPG message
bool          ppg_in_loop     =       true;     // [true/false]   Flag for determening whether PPG is handled in a loop or a timer

// Interface
int           buzz_duty       =       0;        // [%]            Duty cycle for controlling the volume of the buzzer
int           beep_start      =       0;        // [ms]           Start of the beep in ms
int           beep_length     =       0;        // [ms]           Length of the beep in ms
bool          beep_flag       =       false;    // [true/false]   Flag indicating whether we have a new beep or not
int           blue_btn_start  =       0;        // [ms]           Start time for when the blue button has been pressed
bool          blue_btn_state  =       false;    // [true/false]   Flag for indicating whether the blue button is pressed or not

// General
volatile int  led_counter     =       0;        // [#]            Used as a counter to keep track of progress with the LED timer
int           pico_led        =       0;        // [0/1]          Variable which shows whether the Pico LED is ON or OFF
float         battery_voltage =       0.00;     // [V]            Variable used for storing the measured votlage of the LION cell

// Testing
bool          plotter         =       false;    // [true/false]   Flag which indicates if the plotter is active for testing purposes

/*
 *      SPO2 SENSOR
 */
DFRobot_MAX30102            spo2_sensor;        // SpO2 Sensor MAX30102

/*
 *      TIMERS 
 */
RPI_PICO_Timer              TimerLED(0);        // Timer for the heartbeat LED                          - Frequency set in setup() - Default 10 Hz
RPI_PICO_Timer              TimerCOM(1);        // Timer for setting the communication rate             - Frequency set in setup() - Default 0.5 kHz
RPI_PICO_Timer              TimerPPG(2);        // Timer for PPG measurements                           - Frequency set in setup() - Default 2 kHz
RPI_PICO_Timer              TimerSEN(3);        // Timer for sensor data acqusition                     - Frequency set in setup() - Default 2 kHz

/*
 *      PWM
 */
RP2040_PWM*                 PWM_Instance[2];    // PWM for the Pico

/*
 *      LED-s
 */
CRGB                        leds[NUM_LEDS];     // LEDs in the front
 

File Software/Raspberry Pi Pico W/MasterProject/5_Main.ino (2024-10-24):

void setup() {
  // Starting up the Serial Monitor
  Serial.begin(SERIAL_BAUDRATE);
  delay(500);
  Serial.println("Starting the configuration...");
  
  // Setting up the ADC resolution
  analogReadResolution(ADC_RES);

  // Configuring all of the pins
  pinMode(PIN_PWR_BTN,    INPUT);
  pinMode(PIN_PWR_LATCH,  OUTPUT);
  pinMode(PIN_SIG_CHARGE, INPUT);
  pinMode(PIN_MCP_CHARGE, INPUT);
  pinMode(PIN_BPM_PWR,    OUTPUT);
  pinMode(PIN_BPM_BTN,    OUTPUT);
  pinMode(PIN_BPM_PUMP,   OUTPUT);
  pinMode(PIN_BPM_VALVE,  OUTPUT);
  pinMode(PIN_MUX_A,      OUTPUT);
  pinMode(PIN_MUX_B,      OUTPUT);
  pinMode(PIN_MUX_C,      OUTPUT);
  pinMode(PIN_ECG_EN,     OUTPUT);
  pinMode(PIN_NEO_LED,    OUTPUT);
  pinMode(PIN_BUZZ,       OUTPUT);
  pinMode(PIN_ENC_A,      INPUT);
  pinMode(PIN_ENC_B,      INPUT);
  pinMode(PIN_ENC_BTN,    INPUT);
  pinMode(PIN_BPM_ANALOG, INPUT);
  pinMode(PIN_ECG_ANALOG, INPUT);
  pinMode(PIN_AUX_ANALOG, INPUT);

  // Configuring I2C0 Pins
  Wire.setSDA(PIN_I2C0_SDA);
  Wire.setSCL(PIN_I2C0_SCL);

  // Configuring I2C0 Pins
  Wire1.setSDA(PIN_I2C1_SDA);
  Wire1.setSCL(PIN_I2C1_SCL);

  // Default pin states that need to be set
  DigitalPinUpdate();

  // Configuring timers

  // LED Timer (LED) - Frequency set in the Parameters section
  if (TimerLED.attachInterruptInterval(LED_PERIOD, LEDHandler))
  {
    sprint("Starting LED Timer OK, millis() = ");
    sprintln(String(millis()));
    sprint("LED timer frequency: ");
    sprintln(String(LED_FREQUENCY));
    sprint("LED timer period: ");
    sprintln(String(LED_PERIOD));
  }
  else
    sprintln("Can't set LED Timer. Select another freq. or timer");
  
  // COM Timer (Communication) - Frequency set in the Parameters section
  if (TimerCOM.attachInterruptInterval(COMM_PERIOD, CommunicationHandler))
  {
    sprint("Starting COM Timer OK, millis() = ");
    sprintln(String(millis()));
    sprint("COM timer frequency: ");
    sprintln(String(COMM_FREQUENCY));
    sprint("COM timer period: ");
    sprintln(String(COMM_PERIOD));
  }
  else
    sprintln("Can't set COM Timer. Select another freq. or timer");

  // SEN Timer (Sensor) - Frequency set in the Parameters section
  if (TimerSEN.attachInterruptInterval(SEN_PERIOD, SenHandler))
  {
    sprint("Starting SEN Timer OK, millis() = ");
    sprintln(String(millis()));
    sprint("SEN timer frequency: ");
    sprintln(String(SAMPLING_FREQUENCY));
    sprint("SEN timer period: ");
    sprintln(String(SEN_PERIOD));
  }
  else
    sprintln("Can't set COM Timer. Select another freq. or timer");
  /*
  // PPG Timer (PPG) - Frequency set in the Parameters section
  if (TimerPPG.attachInterruptInterval(SEN_PERIOD, PPGHandler))
  {
    sprint("Starting PPG Timer OK, millis() = ");
    sprintln(String(millis()));
    sprint("SEN timer frequency: ");
    sprintln(String(SAMPLING_FREQUENCY));
    sprint("SEN timer period: ");
    sprintln(String(SEN_PERIOD));
  }
  else
    sprintln("Can't set PPG Timer. Select another freq. or timer");*/

  // Setting up PWM
  // BPM Pump
  PWM_Instance[0] = new RP2040_PWM(PIN_BPM_PUMP, PWM_FREQUENCY, 0.00f);
  PWM_Instance[0]->setPWM();
  // Buzzer
  PWM_Instance[1] = new RP2040_PWM(PIN_BUZZ, PWM_FREQUENCY, 0.00f);
  PWM_Instance[1]->setPWM();

  // Configuring the LEDs
  FastLED.addLeds<WS2813, PIN_NEO_LED, RGB>(leds, NUM_LEDS);
  // Turn OFF all of the LEDs in the start
  LED_OFF();

  sprintln("Configuration done, starting the system...");
}
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

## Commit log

2024-10-26 PPG Clamp CAD Files
    [Axle Mount.stl, Cover V1 Half 1.stl, Cover V1 Half 2.stl, Lower Body.stl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]
2024-10-26 STL CAD Files
    [AUX Sign and Ring.stl, Air Pump Mount.stl, Audio Jack Mounting Bracket.stl, Body Bottom Part V1.stl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]
2025-01-07 Add directory for Data and Data Analysis
    Added 2 datasets with codes used to analyze the data and all of the figures and results (including the results from a commercial device). Outside this folder is the latest version of the code used to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
    [FullMeasurement1.csv, VideoFullTest.csv]
2025-09-15 Added PCB Project file
    Added the EasyEDA Pro project file to the electronics directory
